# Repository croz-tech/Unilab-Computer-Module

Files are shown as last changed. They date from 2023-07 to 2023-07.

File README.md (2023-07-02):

# Unilab Computer Module
This is a clone of the UNILAB BBC Micro computer interface. 
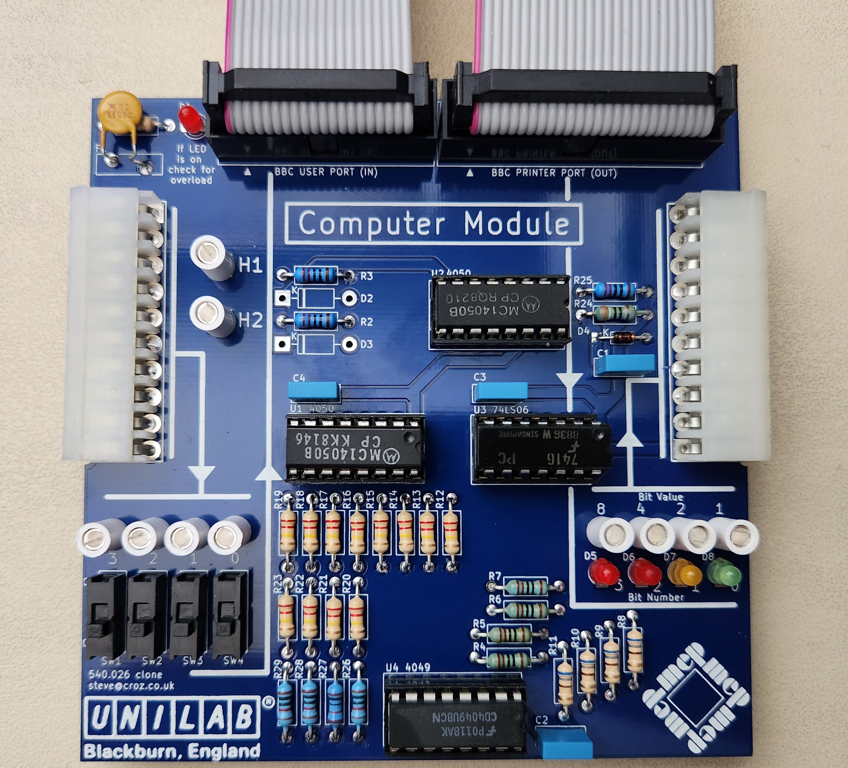
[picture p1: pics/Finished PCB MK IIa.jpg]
Clone Unilab Computer Module

Compatible with all UNILAB modules this allows control from a BBC Micro rateher than the usual 3-Chip-Plus.  This device connects to both PA and PB of the 6522 interface adapter (BBC User Port for input and BBC Printer Port for output).  Credit goes to Louis Higgins who shared detailed photographs of both sides from an original board, enabling this clone to be created.  You'll note that this board is smaller than the original.  While my 3-Chip-Plus clone kept the original board dimensions, this recieved mixed feelings.  In this case I've compressed the board to just 100x100mm to keep it to the $5 level for most board manufacturers. 
 
Example code to read/write these ports from BASIC is included on the schematic.  
## Compatibility:
This board should work fine with the BBC Micro (model B), the B+ range and the Master range, although I think the Master Compact lacks the user port so this is probably incompatible with that machine.

## Notes and Errors:
Note that is the first issue of this schematic/board there are a couple of errors (both to be corrected on a future revision):
1) U3 should be the TTL IC 7416, not 74LS06 as shown on the schematic and PCB skilscreen. 
2) The 3x notches for each of the female connectors (U1 and U4) are on the wrong layer of the PCB design so will be missing on manfuacture.  Use a small round file on the boards to add these notches (shown on the silkscreen) before assembly.

Note also that I have decided to not fit the diodes D2 and D3 from the CB1/CB2 ports to VREF on my first build.  While this might make sense to clamp the H1/H2 inputs (converting to TTL levels safe for the Beeb) I'm concerned that CB1/CB2 can be driven as outputs which might stress the 6522.  Will check on the 6522 datasheet and address this later.

## Connection:
The module connects to the Beeb's User and Printer ports using a 20-way and 26-way IDC ribbon cables respectively.  Unlike the original I've gone with IDC headers rather than IDC solder terminators on the PCB since these are becoming more difficult to get hold of and it means the cables can be entirely removed from the board for easier storage.    I've made the cable around 0.5m length and these are 1:1 cables (pin numbering identical at either end).  The unit takes its power from the Beeb's User Port and can also power UNILAB peripheral boards.  The board is fitted with a 500mA polyfuse to protect the Beeb from any short circuits (the original boards used a 1/4 inch glass fuse).

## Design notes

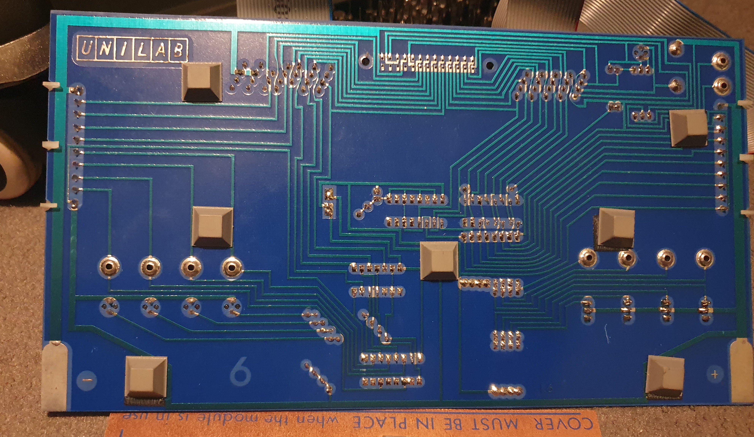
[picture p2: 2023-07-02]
pics/original unilab computer module back.jpg

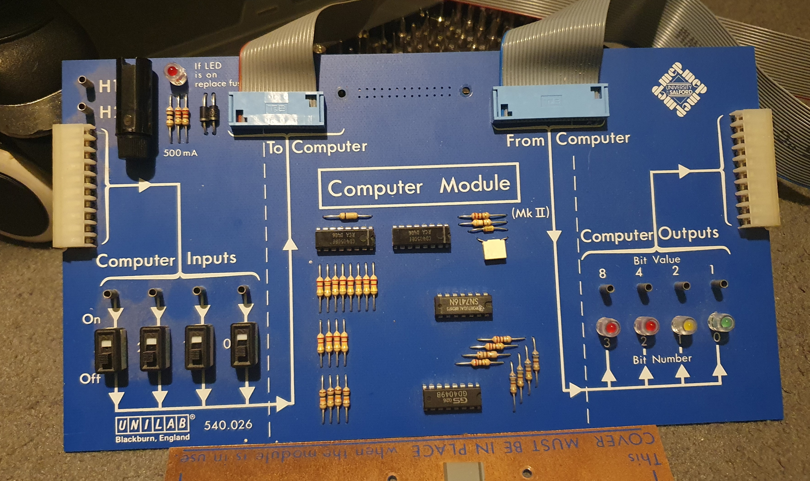
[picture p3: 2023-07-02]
pics/original unliab computer module front.jpg

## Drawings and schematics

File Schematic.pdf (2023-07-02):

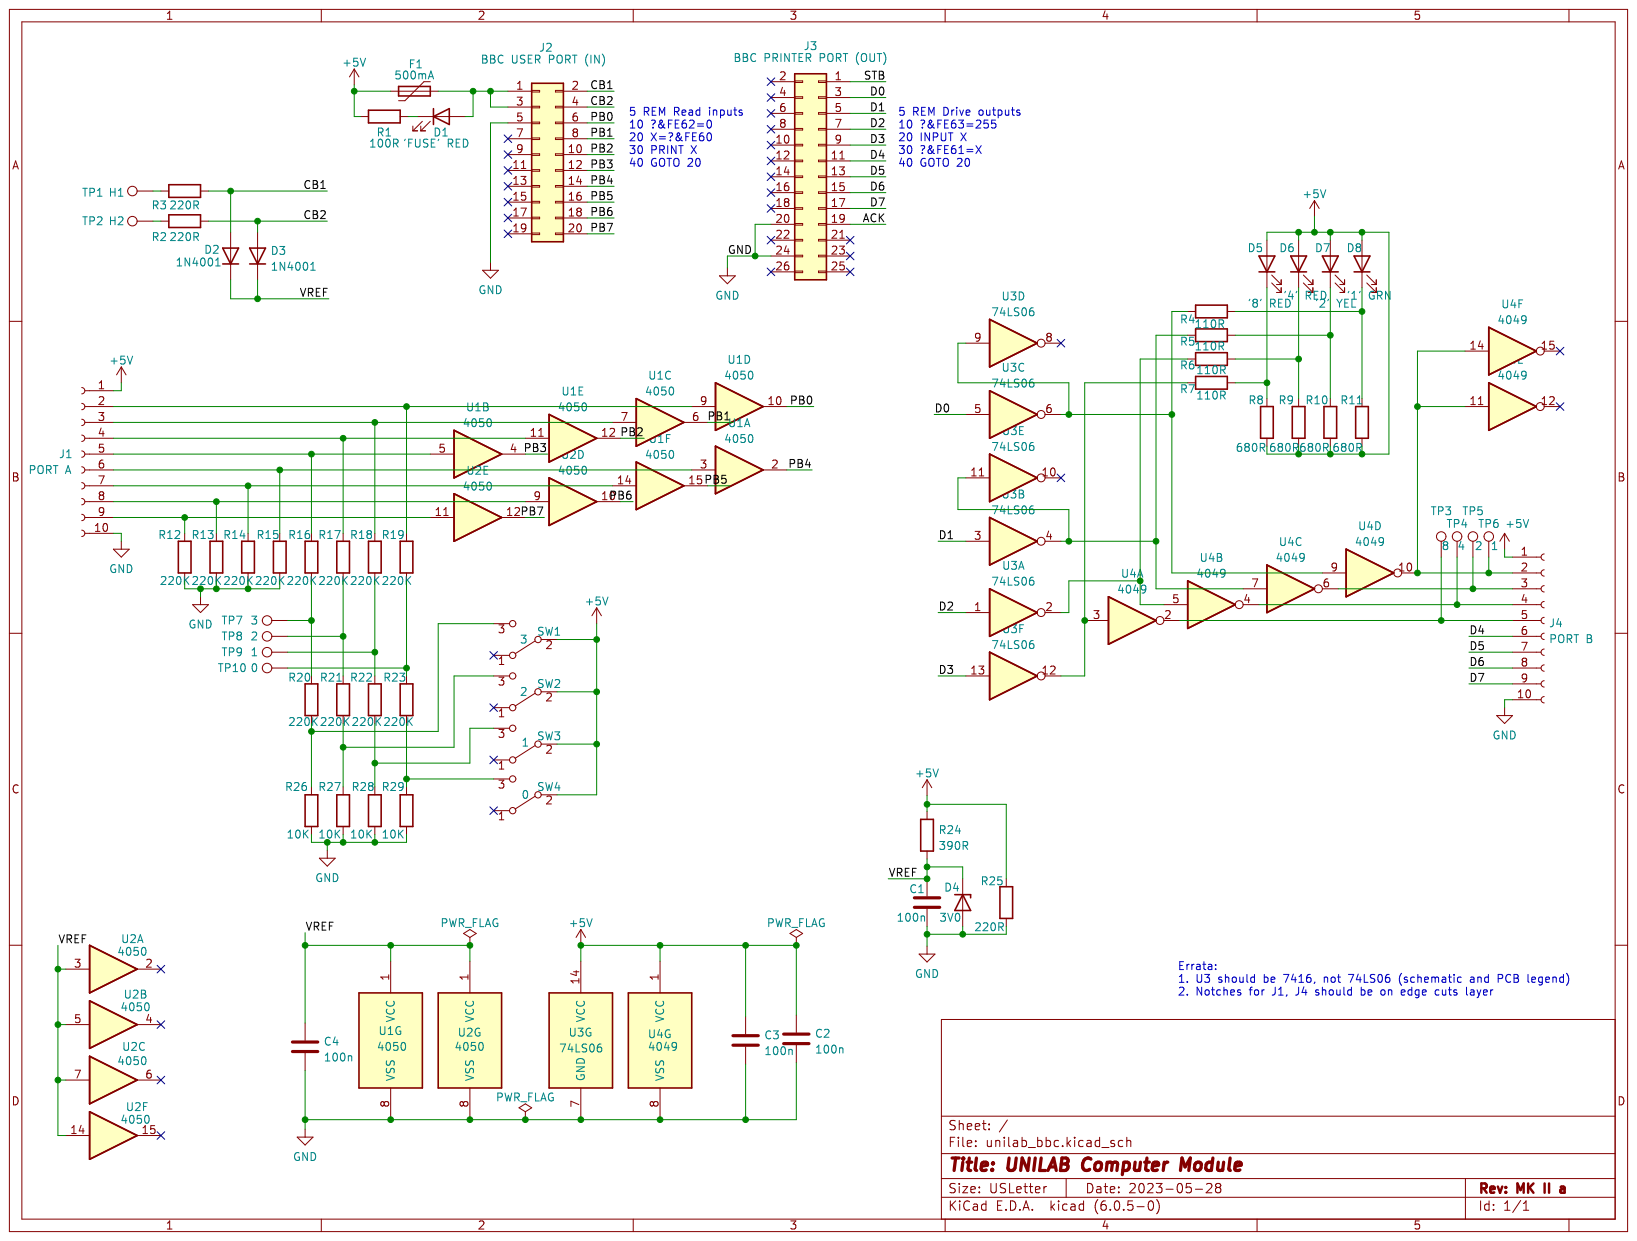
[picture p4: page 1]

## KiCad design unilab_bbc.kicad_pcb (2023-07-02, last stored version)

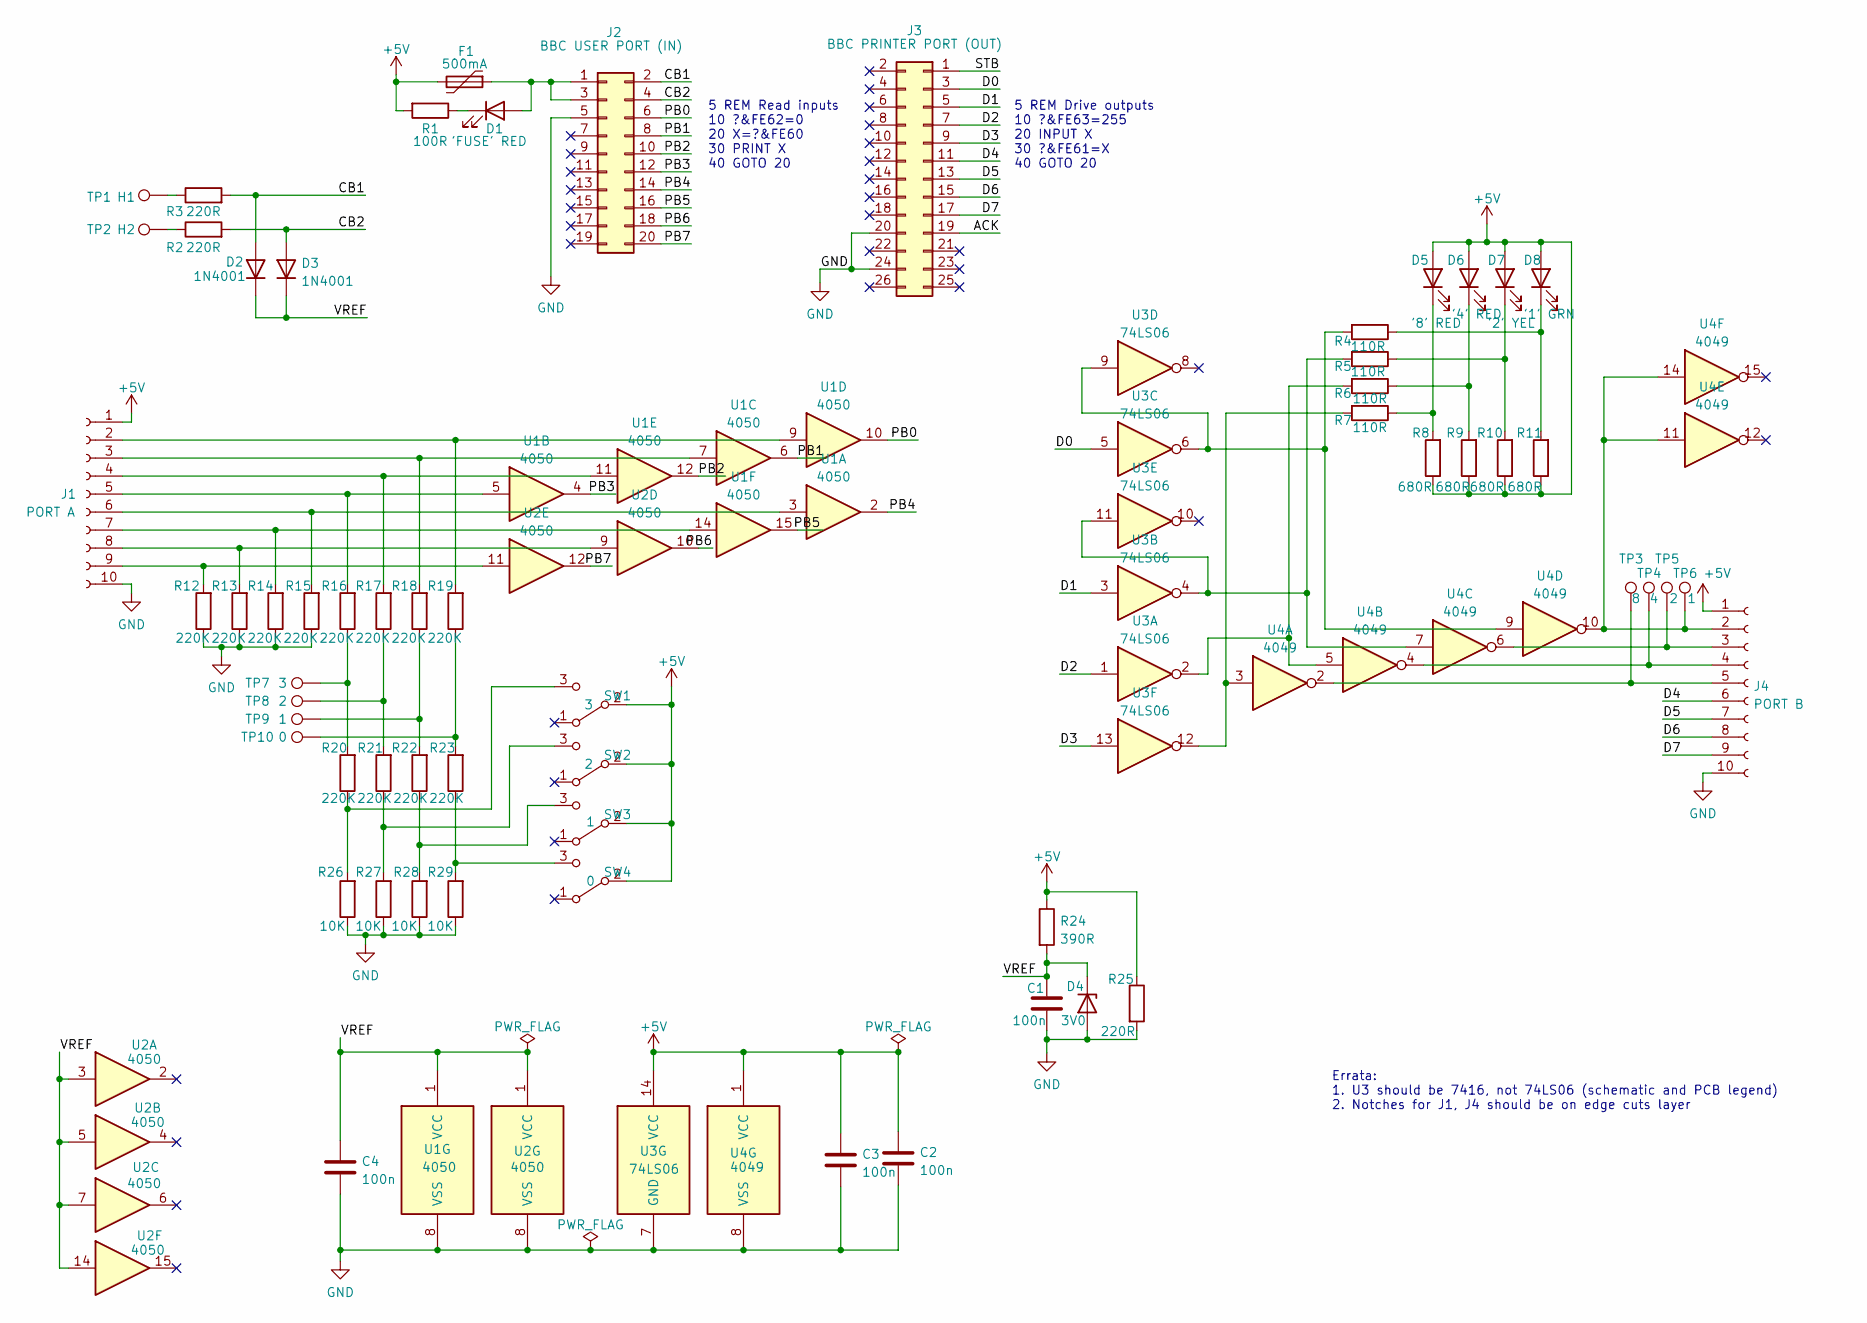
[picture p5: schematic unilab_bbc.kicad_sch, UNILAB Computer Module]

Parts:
C1, C2, C3, C4: 100n; C_Rect_L7.2mm_W2.5mm_P5.00mm_FKS2_FKP2_MKS2_MKP2
D1: 'FUSE' RED; LED_D3.0mm
D2, D3: 1N4001; D_DO-41_SOD81_P10.16mm_Horizontal
D4: 3V0; D_DO-34_SOD68_P7.62mm_Horizontal
D5: '8' RED; LED_D3.0mm
D6: '4' RED; LED_D3.0mm
D7: '2' YEL; LED_D3.0mm
D8: '1' GRN; LED_D3.0mm
F1: 500mA; Fuse_Bourns_MF-RG400
J1: PORT A; 10W_RA_Female
J2: BBC USER PORT (IN); PinHeader_2x10_P2.54mm_Vertical
J3: BBC PRINTER PORT (OUT); PinHeader_2x13_P2.54mm_Vertical
J4: PORT B; 10W_RA_Female
R1: 100R; R_Axial_DIN0207_L6.3mm_D2.5mm_P10.16mm_Horizontal
R2, R3, R25: 220R; R_Axial_DIN0207_L6.3mm_D2.5mm_P10.16mm_Horizontal
R4, R5, R6, R7: 110R; R_Axial_DIN0207_L6.3mm_D2.5mm_P10.16mm_Horizontal
R8, R9, R10, R11: 680R; R_Axial_DIN0207_L6.3mm_D2.5mm_P10.16mm_Horizontal
R12, R13, R14, R15, R16, R17, R18, R19, R20, R21, R22, R23: 220K; R_Axial_DIN0207_L6.3mm_D2.5mm_P10.16mm_Horizontal
R24: 390R; R_Axial_DIN0207_L6.3mm_D2.5mm_P10.16mm_Horizontal
R26, R27, R28, R29: 10K; R_Axial_DIN0207_L6.3mm_D2.5mm_P10.16mm_Horizontal
SW1: 3; SPDT SIP SLIDE
SW2: 2; SPDT SIP SLIDE
SW3: 1; SPDT SIP SLIDE
SW4: 0; SPDT SIP SLIDE
TP1: H1; TestPoint_THTPad_3.0x3.0mm_Drill1.5mm
TP2: H2; TestPoint_THTPad_3.0x3.0mm_Drill1.5mm
TP3: 8; TestPoint_THTPad_D3.0mm_Drill1.5mm
TP4: 4; TestPoint_THTPad_D3.0mm_Drill1.5mm
TP5, TP8: 2; TestPoint_THTPad_D3.0mm_Drill1.5mm
TP6, TP9: 1; TestPoint_THTPad_D3.0mm_Drill1.5mm
TP7: 3; TestPoint_THTPad_D3.0mm_Drill1.5mm
TP10: 0; TestPoint_THTPad_D3.0mm_Drill1.5mm
U1, U2: 4050; DIP-16_W7.62mm_Socket_LongPads
U3: 74LS06; DIP-14_W7.62mm_Socket_LongPads
U4: 4049; DIP-16_W7.62mm_Socket_LongPads

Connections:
+5V: C2.1, C3.1, D5.2 (A), D6.2 (A), D7.2 (A), D8.2 (A), F1.2, J1.1, J4.1, R1.2, R8.1, R9.1, R10.1, R11.1, R24.1, R25.1, SW1.2 (B), SW2.2 (B), SW3.2 (B), SW4.2 (B), U3.14 (VCC), U4.1 (VCC)
/ACK: J3.19
/CB1: D2.2 (A), J2.2, R3.2
/CB2: D3.2 (A), J2.4, R2.2
/D0: J3.3, U3.5
/D1: J3.5, U3.3
/D2: J3.7, U3.1
/D3: J3.9, U3.13
/D4: J3.11, J4.6
/D5: J3.13, J4.7
/D6: J3.15, J4.8
/D7: J3.17, J4.9
/PB0: J2.6, U1.10
/PB1: J2.8, U1.6
/PB2: J2.10, U1.12
/PB3: J2.12, U1.4
/PB4: J2.14, U1.2
/PB5: J2.16, U1.15
/PB6: J2.18, U2.10
/PB7: J2.20, U2.12
/STB: J3.1
/VREF: C1.1, C4.1, D2.1 (K), D3.1 (K), D4.1 (K), R24.2, U1.1 (VCC), U2.1 (VCC), U2.3, U2.5, U2.7, U2.14
GND: C1.2, C2.2, C3.2, C4.2, D4.2 (A), J1.10, J2.5, J3.20, J3.24, J4.10, R12.1, R13.1, R14.1, R15.1, R25.2, R26.1, R27.1, R28.1, R29.1, U1.8 (VSS), U2.8 (VSS), U3.7 (GND), U4.8 (VSS)
unnamed: D1.1 (K), R1.1
unnamed: D1.2 (A), F1.1, J2.1, J2.3
unnamed: D5.1 (K), R7.1, R8.2
unnamed: D6.1 (K), R6.1, R9.2
unnamed: D7.1 (K), R5.1, R10.2
unnamed: D8.1 (K), R4.1, R11.2
unnamed: J1.2, R19.2, U1.9
unnamed: J1.3, R18.2, U1.7
unnamed: J1.4, R17.2, U1.11
unnamed: J1.5, R16.2, U1.5
unnamed: J1.6, R15.2, U1.3
unnamed: J1.7, R14.2, U1.14
unnamed: J1.8, R13.2, U2.9
unnamed: J1.9, R12.2, U2.11
unnamed: J4.2, TP6.1, U4.10, U4.11, U4.14
unnamed: J4.3, TP5.1, U4.6
unnamed: J4.4, TP4.1, U4.4
unnamed: J4.5, TP3.1, U4.2
unnamed: R2.1, TP2.1
unnamed: R3.1, TP1.1
unnamed: R4.2, U3.6, U3.9, U4.9
unnamed: R5.2, U3.4, U3.11, U4.7
unnamed: R6.2, U3.2, U4.5
unnamed: R7.2, U3.12, U4.3
unnamed: R16.1, R20.2, TP7.1
unnamed: R17.1, R21.2, TP8.1
unnamed: R18.1, R22.2, TP9.1
unnamed: R19.1, R23.2, TP10.1
unnamed: R20.1, R26.2, SW1.3 (C)
unnamed: R21.1, R27.2, SW2.3 (C)
unnamed: R22.1, R28.2, SW3.3 (C)
unnamed: R23.1, R29.2, SW4.3 (C)

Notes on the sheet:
5 REM Drive outputs 10 ?&FE63=255 20 INPUT X 30 ?&FE61=X 40 GOTO 20
Errata: 1. U3 should be 7416, not 74LS06 (schematic and PCB legend) 2. Notches for J1, J4 should be on edge cuts layer
5 REM Read inputs 10 ?&FE62=0 20 X=?&FE60 30 PRINT X 40 GOTO 20

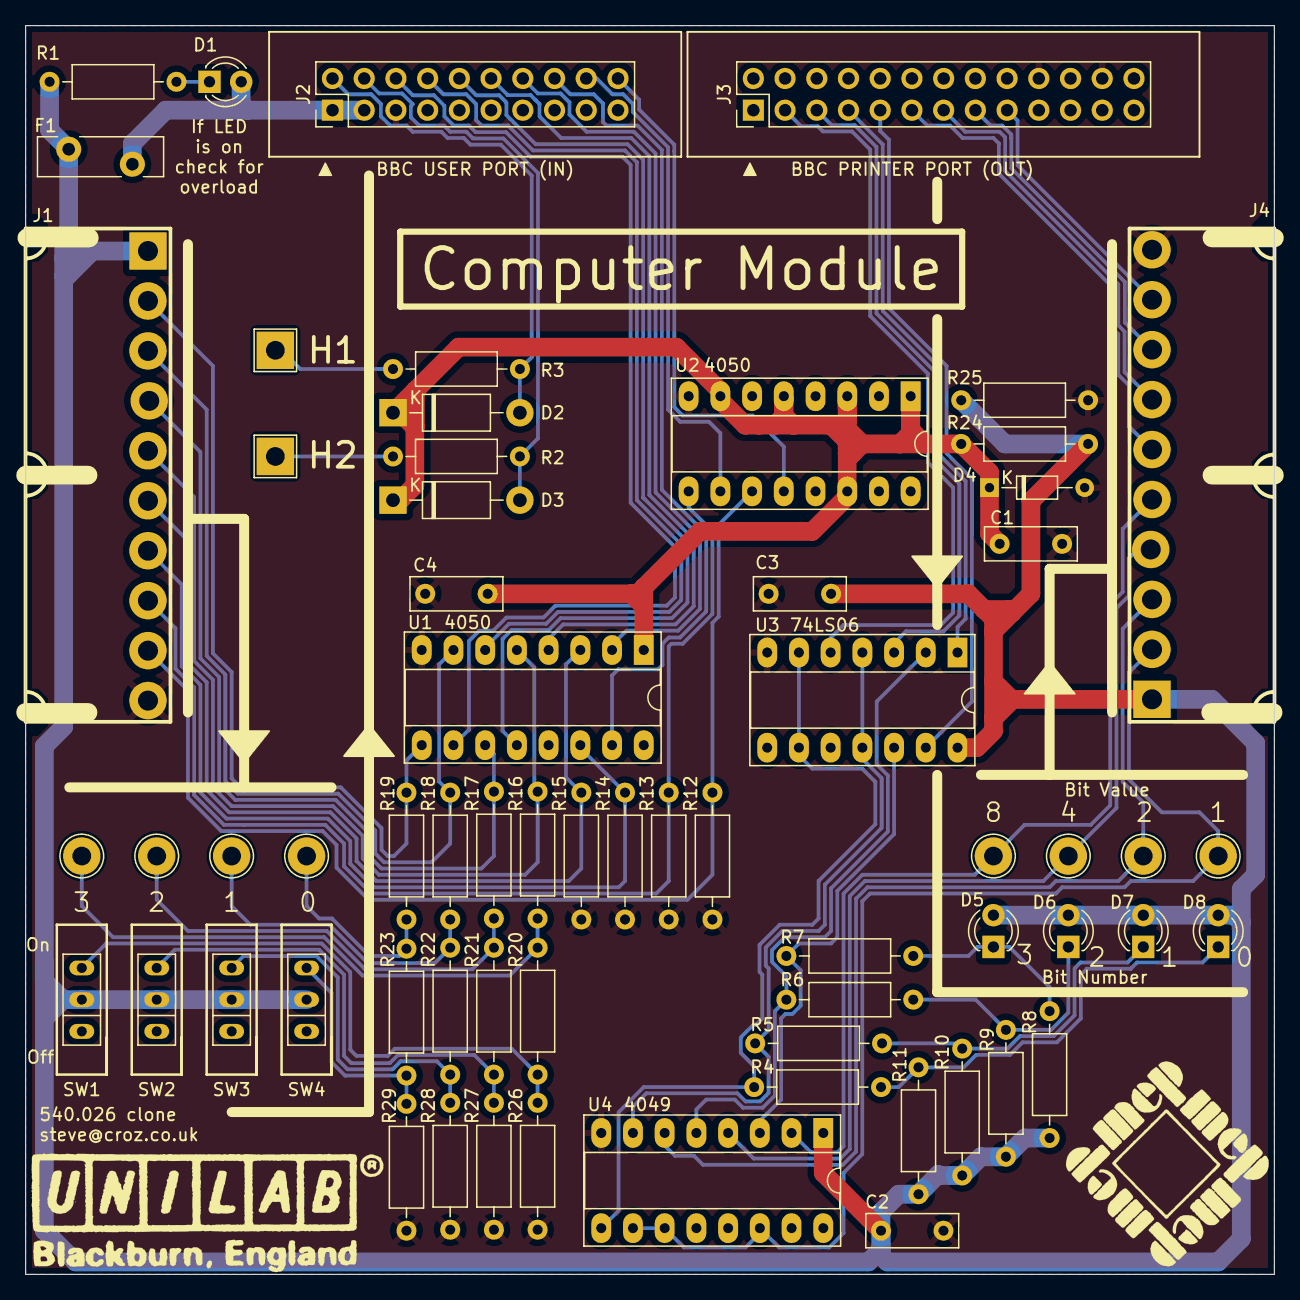
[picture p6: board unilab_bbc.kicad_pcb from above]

Board: 2 copper layers, 100.0 x 100.0 mm, 64 parts (0 on the bottom side), 53 nets.

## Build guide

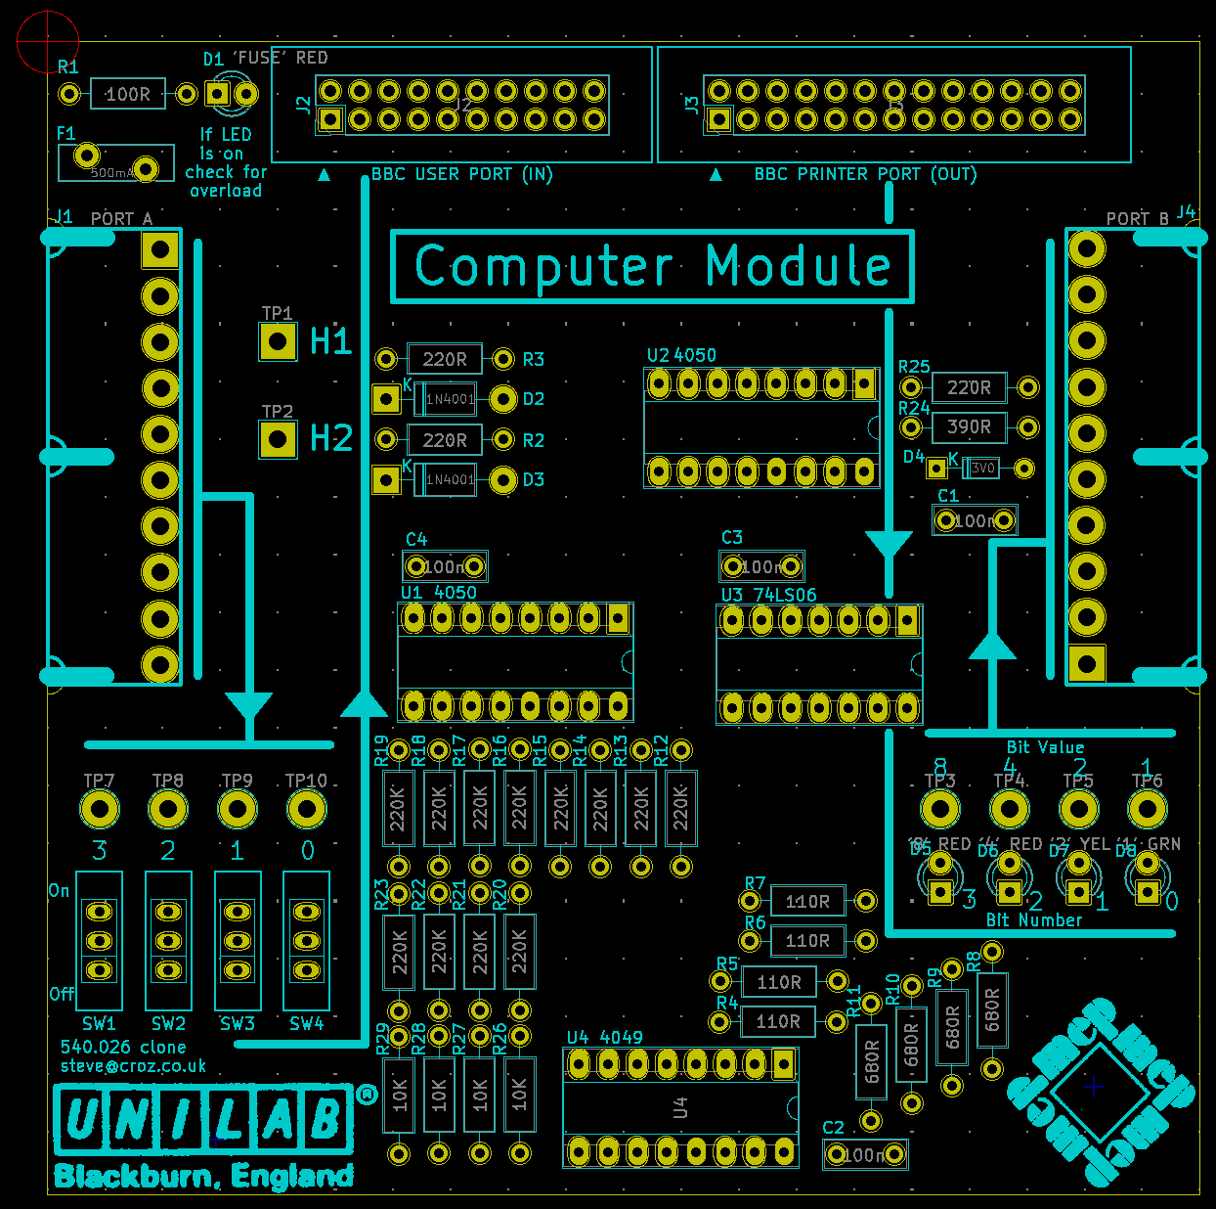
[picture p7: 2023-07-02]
Fabrication.png
